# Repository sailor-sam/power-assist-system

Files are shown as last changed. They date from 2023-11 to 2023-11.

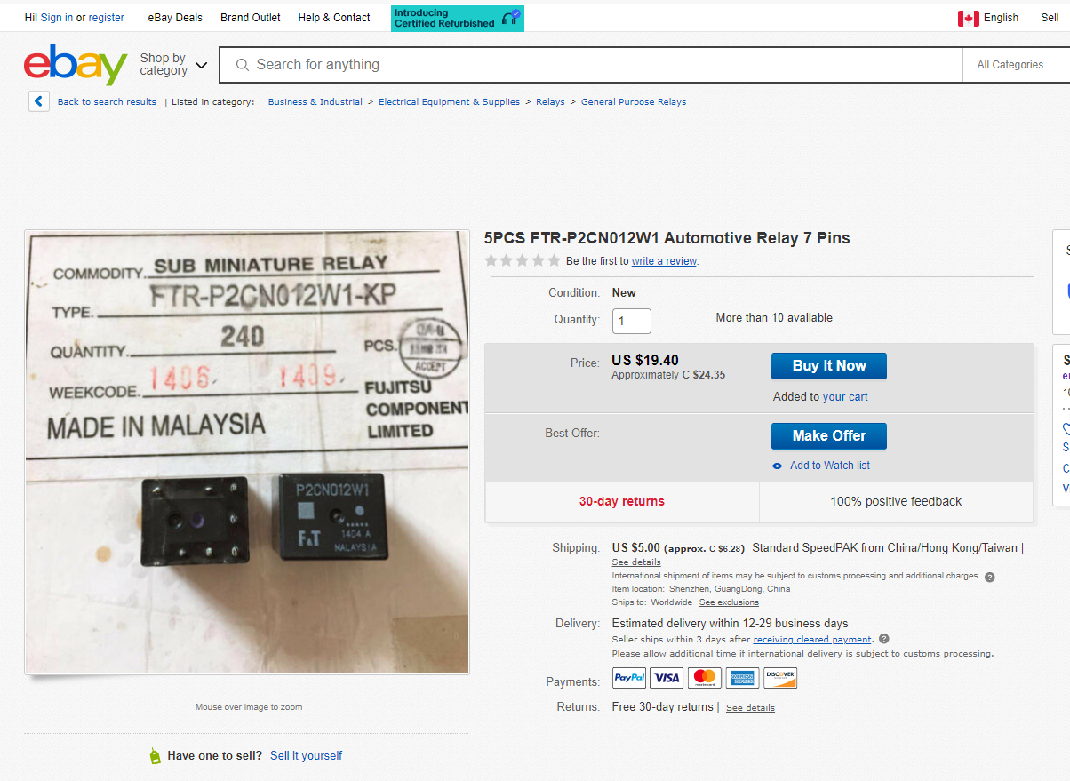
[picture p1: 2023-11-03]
module design files/joystick/Arduino_MKVI development/Fujitsu P2CN012W1 relay EBay.png

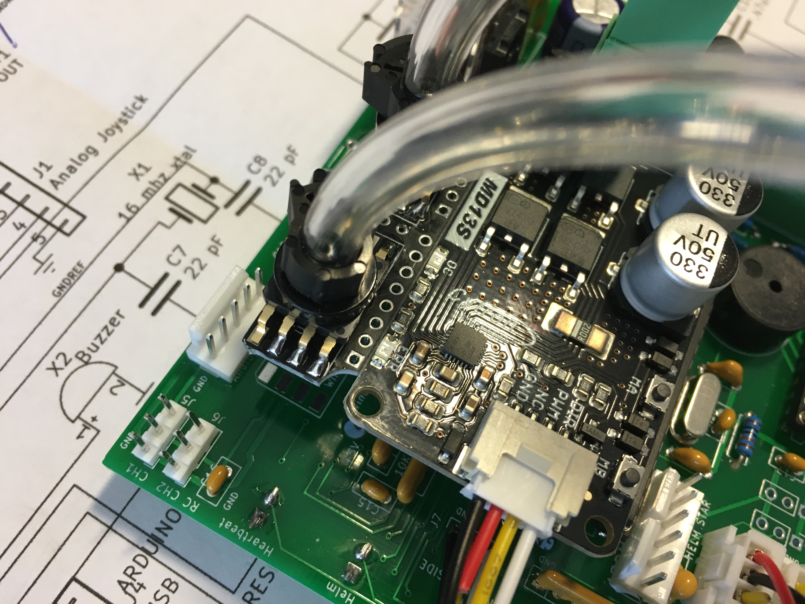
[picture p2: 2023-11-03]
module design files/joystick/Mk VI photos/MkVI SnP orientation 2.JPG

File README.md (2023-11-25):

# power-assist-system
Electronic servo motor system designed to assist people with severe  disabilities to control the helm and sail sheeting systems of a small  sailboat, via a sip&amp;puff or medical joystick interface.

Kevin and Rick Mercer

https://youtu.be/U6-sZrs9T38?si=PjePZXyoL59SkXcZ&t=115

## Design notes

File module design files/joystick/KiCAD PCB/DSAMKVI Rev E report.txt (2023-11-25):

Plot file "C:\Data files\Power Assist System\Product Design & Revision files\Mk VI Redesign 2023\DSAMKVIA KiCad\DSAMKVI REV B - E\DSAMKVIE-F_Cu.gbr" created.
Plot file "C:\Data files\Power Assist System\Product Design & Revision files\Mk VI Redesign 2023\DSAMKVIA KiCad\DSAMKVI REV B - E\DSAMKVIE-B_Cu.gbr" created.
Plot file "C:\Data files\Power Assist System\Product Design & Revision files\Mk VI Redesign 2023\DSAMKVIA KiCad\DSAMKVI REV B - E\DSAMKVIE-F_Paste.gbr" created.
Plot file "C:\Data files\Power Assist System\Product Design & Revision files\Mk VI Redesign 2023\DSAMKVIA KiCad\DSAMKVI REV B - E\DSAMKVIE-B_Paste.gbr" created.
Plot file "C:\Data files\Power Assist System\Product Design & Revision files\Mk VI Redesign 2023\DSAMKVIA KiCad\DSAMKVI REV B - E\DSAMKVIE-F_SilkS.gbr" created.
Plot file "C:\Data files\Power Assist System\Product Design & Revision files\Mk VI Redesign 2023\DSAMKVIA KiCad\DSAMKVI REV B - E\DSAMKVIE-F_Mask.gbr" created.
Plot file "C:\Data files\Power Assist System\Product Design & Revision files\Mk VI Redesign 2023\DSAMKVIA KiCad\DSAMKVI REV B - E\DSAMKVIE-B_Mask.gbr" created.
Plot file "C:\Data files\Power Assist System\Product Design & Revision files\Mk VI Redesign 2023\DSAMKVIA KiCad\DSAMKVI REV B - E\DSAMKVIE-Edge_Cuts.gbr" created.

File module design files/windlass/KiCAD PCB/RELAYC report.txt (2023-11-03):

Plot file "C:\Data files\Power Assist System\Product Design & Revision files\Mk VI design\RELAYB\RELAYC-F_Cu.gbr" created.
Plot file "C:\Data files\Power Assist System\Product Design & Revision files\Mk VI design\RELAYB\RELAYC-B_Cu.gbr" created.
Plot file "C:\Data files\Power Assist System\Product Design & Revision files\Mk VI design\RELAYB\RELAYC-F_Paste.gbr" created.
Plot file "C:\Data files\Power Assist System\Product Design & Revision files\Mk VI design\RELAYB\RELAYC-B_Paste.gbr" created.
Plot file "C:\Data files\Power Assist System\Product Design & Revision files\Mk VI design\RELAYB\RELAYC-F_SilkS.gbr" created.
Plot file "C:\Data files\Power Assist System\Product Design & Revision files\Mk VI design\RELAYB\RELAYC-F_Mask.gbr" created.
Plot file "C:\Data files\Power Assist System\Product Design & Revision files\Mk VI design\RELAYB\RELAYC-B_Mask.gbr" created.
Plot file "C:\Data files\Power Assist System\Product Design & Revision files\Mk VI design\RELAYB\RELAYC-Edge_Cuts.gbr" created.

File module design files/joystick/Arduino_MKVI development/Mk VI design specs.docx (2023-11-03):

3/31/21 pin 27 and 28 can be used for I2C in future

Pin | Description | 328Pin | UNO | Description | Function REVC
| +5V | 1 | RESET | PC6 | Reset
4 | USB TXD (or) Program Mode button | 2 | 0 | PD0 – IN | Digital Pin (RX)
5 | USB RXD | 3 | 1 | PD1 – OUT | Digital Pin (TX)
37 | RC1_input | 4 | 2 | PB0 – IN | Digital Pin
38 | RC2_input | 5 | 3 | PB1 – IN | Digital Pin (PWM)
23 | BUZZER | 6 | 4 | PD2 – OUT | Digital Pin
11 | VDD | 7 | | Vcc | Positive Voltage (Power)
12 | GND | 8 | | GND | Ground
13 | XTAL 1 | 9 | | XTAL 1 | Crystal Oscillator
14 | XTAL 2 | 10 | | XTAL 2 | Crystal Oscillator
21 | Windlass_LMP | 11 | 5 | PD5 – OUT | Digital Pin (PWM)
18 | Winch_OUT | 12 | 6 | PD6 – OUT | Digital Pin (PWM)
17 | Winch_IN | 13 | 7 | PD7 – OUT | Digital Pin
16 | PWM1_direction | 14 | 8 | PD3 – OUT | Digital Pin
15 | PWM1 helm | 15 | 9 | PD4 – OUT | Digital Pin (PWM)
22 | Bat_LOW_LED | 16 | 10 | PB2 – OUT | Digital Pin (PWM)
27 | Winch_LED | 17 | 11 | PB3 – OUT | Digital Pin (PWM)
28 | Helm_LED | 18 | 12 | PB4 – OUT | Digital Pin
29 | Heartbeat_LED | 19 | 13 | PB5 – OUT | Digital Pin
?? | AVCC | 20 | | AVCC | Positive voltage for ADC (power)
5 | Vref joystick | 21 | | AREF – IN | ADC Ref Voltage = Vcc
31 | GND | 22 | | GND | Ground
2 | Joystick helm | 23 | A0 | PC0 – IN | Analog Input
3 | Joystick wind | 24 | A1 | PC1 – IN | Analog Input
| S/P helm | 25 | A2 | PC2 – IN | Analog Input
| S/P wind | 26 | A3 | PC3 – IN | Analog Input
| Bat sensor | 27 | A4 | PC4 – IN | Analog Input SDA
4 | MODE | 28 | A5 | PC5 – IN | Analog Input SCL

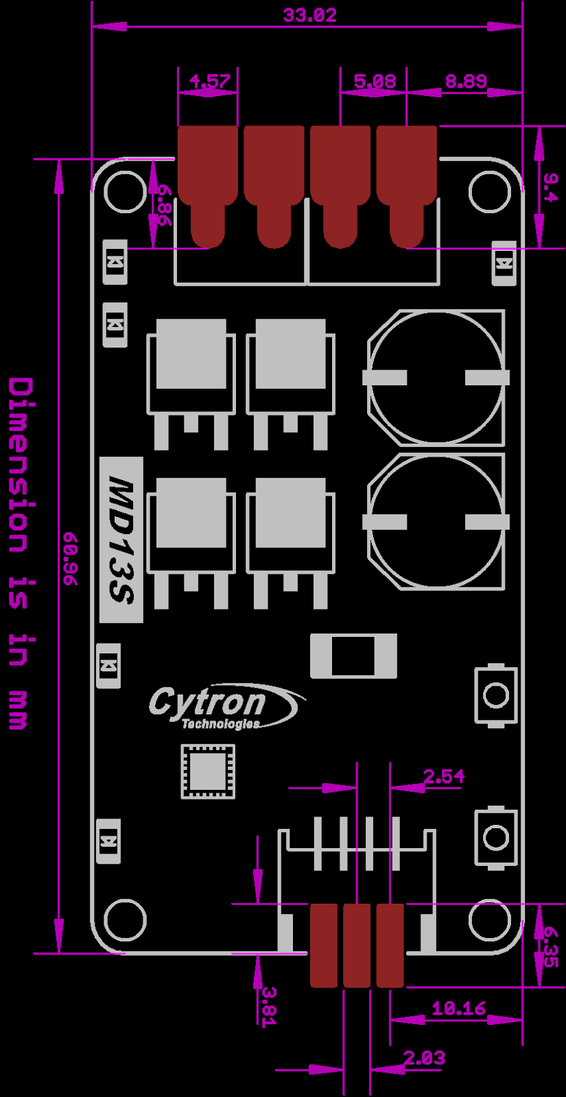
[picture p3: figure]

Remote RC: RadioLink T8S transmitter and R8EF Receiver

T8S transmitter must be configured via the RadioLink IPhone App.

Channels: For T8S, channels ONE (RC1 HELM) and THREE (RC2 WINCH) are connected to Mk VI PCB ports. Note that polarity of both T8S channels must be REVERSED.

RX Failsafe Mode: As long as it is powered by the mk VI, the R8EF cannot be configured to stop transmitting pulses to the Mk VI, whether or not a TX is present. Failsafe Mode (F/S) is set at 50% PWM. When TX is turned OFF (or out of range), PWM will be NEUTRAL and not interfere with joystick/sip and puff commands.

NOTE: while using RadioLink App, settings can only be changed when TX is disconnected (go figure!). 1) READ configuration from TX, 2) then DISCONNECT, 3) make changes, 4) then RECONNECT and WRITE changes to TX.

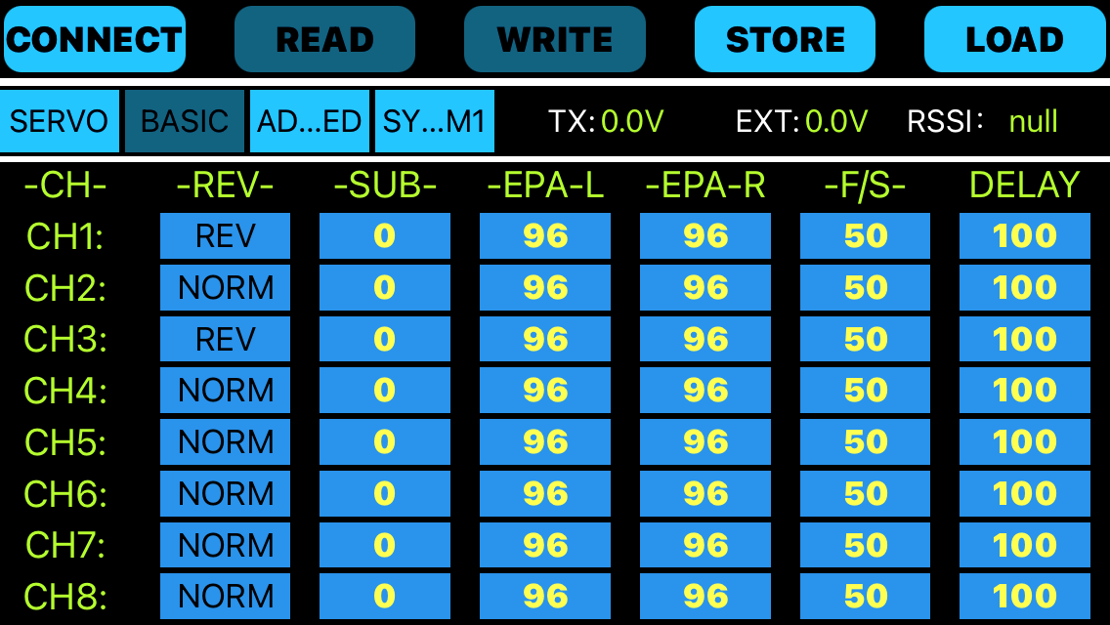
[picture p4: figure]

ATMega328 pinout

In this article, we will go over the pinout of the Atmega328 chip.

The Atmega328 is a very popular microcontroller chip produced by Atmel. It is an 8-bit microcontroller that has 32K of flash memory, 1K of EEPROM, and 2K of internal SRAM.

The Atmega328 is one of the microcontroller chips that are used with the popular Arduino Duemilanove boards. The Arduino Duemilanove board comes with either 1 of 2 microcontroller chips, the Atmega168 or the Atmega328. Of these 2, the Atmega328 is the upgraded, more advanced chip. Unlike the Atmega168 which has 16K of flash program memory and 512 bytes of internal SRAM, the Atmega328 has 32K of flash program memory and 2K of Internal SRAM.

The Atmega328 has 28 pins.

It has 14 digital I/O pins, of which 6 can be used as PWM outputs and 6 analog input pins. These I/O pins account for 20 of the pins.

The pinout for the Atmega328 is shown below.

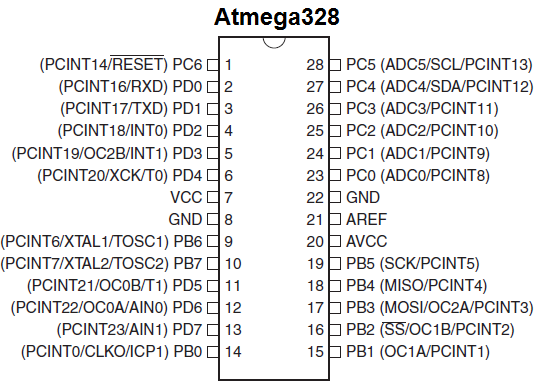
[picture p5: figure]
Atmega328 pinout

The table below gives a description for each of the pins, along with their function.

Pin Number | Description | Function
1 | PC6 | Reset
2 | PD0 | Digital Pin (RX)
3 | PD1 | Digital Pin (TX)
4 | PD2 | Digital Pin – EXT INT
5 | PD3 | Digital Pin (PWM) – EXT INT
6 | PD4 | Digital Pin
7 | Vcc | Positive Voltage (Power)
8 | GND | Ground
9 | XTAL 1 | Crystal Oscillator
10 | XTAL 2 | Crystal Oscillator
11 | PD5 | Digital Pin (PWM)
12 | PD6 | Digital Pin (PWM)
13 | PD7 | Digital Pin
14 | PB0 | Digital Pin
15 | PB1 | Digital Pin (PWM)
16 | PB2 | Digital Pin (PWM)
17 | PB3 | Digital Pin (PWM)
18 | PB4 | Digital Pin
19 | PB5 | Digital Pin
20 | AVCC | Positive voltage for ADC (power)
21 | AREF | Reference Voltage
22 | GND | Ground
23 | PC0 | Analog Input
24 | PC1 | Analog Input
25 | PC2 | Analog Input
26 | PC3 | Analog Input
27 | PC4 | Analog Input - I2C SDA
28 | PC5 | Analog Input – I2C SCL

As stated before, 20 of the pins function as I/O ports. This means they can function as an input to the circuit or as output. Whether they are input or output is set in the software. 14 of the pins are digital pins, of which 6 can function to give PWM output. 6 of the pins are for analog input/output.

2 of the pins are for the crystal oscillator. This is to provide a clock pulse for the Atmega chip. A clock pulse is needed for synchronization so that communication can occur in synchrony between the Atmega chip and a device that it is connected to.

The chip needs power so 2 of the pins, Vcc and GND, provide it power so that it can operate. The Atmega328 is a low-power chip, so it only needs between 1.8-5.5V of power to operate.

The Atmega328 chip has an analog-to-digital converter (ADC) inside of it. This must be or else the Atmega328 wouldn't be capable of interpreting analog signals. Because there is an ADC, the chip can interpret analog input, which is why the chip has 6 pins for analog input. The ADC has 3 pins set aside for it to function- AVCC, AREF, and GND. AVCC is the power supply, positive voltage, that for the ADC. The ADC needs its own power supply in order to work. GND is the power supply ground. AREF is the reference voltage that the ADC uses to convert an analog signal to its corresponding digital value. Analog voltages higher than the reference voltage will be assigned to a digital value of 1, while analog voltages below the reference voltage will be assigned the digital value of 0. Since the ADC for the Atmega328 is a 10-bit ADC, meaning it produces a 10-bit digital value, it converts an analog signal to its digital value, with the AREF value being a reference for which digital values are high or low. Thus, a portrait of an analog signal is shown by this digital value; thus, it is its digital correspondent value.

The last pin is the RESET pin. This allows a program to be rerun and start over.

And this sums up the pinout of an Atmega328 chip.

Related Resources

How to Use the LM741 Op Amp as a Comparator (http://www.learningaboutelectronics.com/Articles/LM741-op-amp-voltage-comparator.php)

How to Build an LM339 Quad Voltage Comparator Circuit (http://www.learningaboutelectronics.com/Articles/LM339-quad-voltage-comparator-circuit.php)

How to Build a Dark-activated Switch (http://www.learningaboutelectronics.com/Articles/Dark-activated-switch.php)

How to Build a Hall Effect Sensor Circuit (http://www.learningaboutelectronics.com/Articles/Hall-effect-sensor-circuit.php)

How to Build a Touch Sensor Circuit (http://www.learningaboutelectronics.com/Articles/How-to-build-a-touch-sensor-circuit)

How to Build an Accelerometer Circuit (http://www.learningaboutelectronics.com/Articles/Accelerometer-circuit.php)

How to Build a Motion Detector Circuit (http://www.learningaboutelectronics.com/Articles/Motion-detector-circuit.php)

How to Build a Motion Detector Alarm Circuit (http://www.learningaboutelectronics.com/Articles/Motion-detector-alarm-circuit.php)

23. Analog-to-Digital Converter

23.1 Features

● 10-bit resolution

● 0.5 LSB integral non-linearity

● ±2 LSB absolute accuracy

● 65 to 260µs conversion time

● Up to 15kSPS

● 6 multiplexed single ended input channels

● 2 additional multiplexed single ended input channels

● Temperature sensor input channel

● Optional left adjustment for ADC result readout

● 0 to VCC ADC input voltage range

● Selectable 1.1V ADC reference voltage

● Free running or single conversion mode

● Interrupt on ADC conversion complete

● Sleep mode noise canceler

23.2 Overview

The Atmel® ATmega328P features a 10-bit successive approximation ADC. The ADC is connected to an 8-channel analog multiplexer which allows eight single-ended voltage inputs constructed from the pins of Port A. The single-ended voltage inputs refer to 0V (GND).

The ADC contains a sample and hold circuit which ensures that the input voltage to the ADC is held at a constant level during conversion. A block diagram of the ADC is shown in Figure 23-1 on page 206.

The ADC has a separate analog supply voltage pin, AVCC. AVCC must not differ more than ±0.3V from VCC. See Section 23.6 “ADC Noise Canceler” on page 211 on how to connect this pin.

Internal reference voltages of nominally 1.1V or AVCC are provided on-chip. The voltage reference may be externally decoupled at the AREF pin by a capacitor for better noise performance.

The power reduction ADC bit, PRADC, in Section 9.10 “Minimizing Power Consumption” on page 36 must be disabled by writing a logical zero to enable the ADC.

The ADC converts an analog input voltage to a 10-bit digital value through successive approximation. The minimum value represents GND and the maximum value represents the voltage on the AREF pin minus 1 LSB.

Optionally, AVCC or an internal 1.1V reference voltage may be connected to the AREF pin by writing to the REFSn bits in the ADMUX register. The internal voltage reference may thus be decoupled by an external capacitor at the AREF pin to improve noise immunity.

# Digital Pins

The pins on the Arduino can be configured as either inputs or outputs. This document explains the functioning of the pins in those modes. While the title of this document refers to digital pins, it is important to note that vast majority of Arduino (Atmega) analog pins, may be configured, and used, in exactly the same manner as digital pins.

### Properties of Pins Configured as INPUT

Arduino (Atmega) pins default to inputs, so they don't need to be explicitly declared as inputs with pinMode() when you're using them as inputs. Pins configured this way are said to be in a high-impedance state. Input pins make extremely small demands on the circuit that they are sampling, equivalent to a series resistor of 100 megohm in front of the pin. This means that it takes very little current to move the input pin from one state to another, and can make the pins useful for such tasks as implementing a capacitive touch sensor (https://www.arduino.cc/playground/Code/CapacitiveSensor), reading an LED as a photodiode (https://www.arduino.cc/playground/Learning/LEDSensor), or reading an analog sensor with a scheme such as RCTime. (https://www.arduino.cc/en/Tutorial/RCtime)

This also means however, that pins configured as pinMode(pin, INPUT) with nothing connected to them, or with wires connected to them that are not connected to other circuits, will report seemingly random changes in pin state, picking up electrical noise from the environment, or capacitively coupling the state of a nearby pin.

### Pullup Resistors with pins configured as INPUT

Often it is useful to steer an input pin to a known state if no input is present. This can be done by adding a pullup resistor (to +5V), or a pulldown resistor (resistor to ground) on the input. A 10K resistor is a good value for a pullup or pulldown resistor.

### Properties of Pins Configured as INPUT_PULLUP

There are 20K pullup resistors built into the Atmega chip that can be accessed from software. These built-in pullup resistors are accessed by setting the pinMode() as INPUT_PULLUP. This effectively inverts the behavior of the INPUT mode, where HIGH means the sensor is off, and LOW means the sensor is on.

The value of this pullup depends on the microcontroller used. On most AVR-based boards, the value is guaranteed to be between 20kΩ and 50kΩ. On the Arduino Due, it is between 50kΩ and 150kΩ. For the exact value, consult the datasheet of the microcontroller on your board.

When connecting a sensor to a pin configured with INPUT_PULLUP, the other end should be connected to ground. In the case of a simple switch, this causes the pin to read HIGH when the switch is open, and LOW when the switch is pressed.

The pullup resistors provide enough current to dimly light an LED connected to a pin that has been configured as an input. If LEDs in a project seem to be working, but very dimly, this is likely what is going on.

The pullup resistors are controlled by the same registers (internal chip memory locations) that control whether a pin is HIGH or LOW. Consequently, a pin that is configured to have pullup resistors turned on when the pin is an INPUT, will have the pin configured as HIGH if the pin is then switched to an OUTPUT with pinMode(). This works in the other direction as well, and an output pin that is left in a HIGH state will have the pullup resistors set if switched to an input with pinMode().

Prior to Arduino 1.0.1, it was possible to configure the internal pull-ups in the following manner:

pinMode(pin, INPUT); // set pin to input

digitalWrite(pin, HIGH); // turn on pullup resistors

NOTE: Digital pin 13 is harder to use as a digital input than the other digital pins because it has an LED and resistor attached to it that's soldered to the board on most boards. If you enable its internal 20k pull-up resistor, it will hang at around 1.7V instead of the expected 5V because the onboard LED and series resistor pull the voltage level down, meaning it always returns LOW. If you must use pin 13 as a digital input, set its pinMode() to INPUT and use an external pull down resistor.

### Properties of Pins Configured as OUTPUT

Pins configured as OUTPUT with pinMode() are said to be in a low-impedance state. This means that they can provide a substantial amount of current to other circuits. Atmega pins can source (provide positive current) or sink (provide negative current) up to 40 mA (milliamps) of current to other devices/circuits. This is enough current to brightly light up an LED (don't forget the series resistor), or run many sensors, for example, but not enough current to run most relays, solenoids, or motors.

Short circuits on Arduino pins, or attempting to run high current devices from them, can damage or destroy the output transistors in the pin, or damage the entire Atmega chip. Often this will result in a "dead" pin in the microcontroller but the remaining chip will still function adequately. For this reason it is a good idea to connect OUTPUT pins to other devices with 470Ω or 1k resistors, unless maximum current draw from the pins is required for a particular application.

# analogRead()

[Analog I/O]

### Description

Reads the value from the specified analog pin. Arduino boards contain a multichannel, 10-bit analog to digital converter. This means that it will map input voltages between 0 and the operating voltage(5V or 3.3V) into integer values between 0 and 1023. On an Arduino UNO, for example, this yields a resolution between readings of: 5 volts / 1024 units or, 0.0049 volts (4.9 mV) per unit. See the table below for the usable pins, operating voltage and maximum resolution for some Arduino boards.

The input range can be changed using analogReference() (https://www.arduino.cc/reference/en/language/functions/analog-io/analogreference), while the resolution can be changed (only for Zero, Due and MKR boards) using analogReadResolution().

On ATmega based boards (UNO, Nano, Mini, Mega), it takes about 100 microseconds (0.0001 s) to read an analog input, so the maximum reading rate is about 10,000 times a second.

BOARD | OPERATING VOLTAGE | USABLE PINS | MAX RESOLUTION
Uno | 5 Volts | A0 to A5 | 10 bits
Mini, Nano | 5 Volts | A0 to A7 | 10 bits
Mega, Mega2560, MegaADK | 5 Volts | A0 to A14 | 10 bits
Micro | 5 Volts | A0 to A11* | 10 bits
Leonardo | 5 Volts | A0 to A11* | 10 bits
Zero | 3.3 Volts | A0 to A5 | 12 bits**
Due | 3.3 Volts | A0 to A11 | 12 bits**
MKR Family boards | 3.3 Volts | A0 to A6 | 12 bits**

*A0 through A5 are labelled on the board, A6 through A11 are respectively available on pins 4, 6, 8, 9, 10, and 12
**The default analogRead() resolution for these boards is 10 bits, for compatibility. You need to use analogReadResolution() (https://www.arduino.cc/reference/en/language/functions/zero-due-mkr-family/analogreadresolution) to change it to 12 bits.

### Syntax

analogRead(pin)

### Parameters

pin: the name of the analog input pin to read from (A0 to A5 on most boards, A0 to A6 on MKR boards, A0 to A7 on the Mini and Nano, A0 to A15 on the Mega).

### Returns

The analog reading on the pin. Although it is limited to the resolution of the analog to digital converter (0-1023 for 10 bits or 0-4095 for 12 bits). Data type: int.

### Example Code

The code reads the voltage on analogPin and displays it.

int analogPin = A3; // potentiometer wiper (middle terminal) connected to analog pin 3

// outside leads to ground and +5V

int val = 0; // variable to store the value read

void setup() {

Serial.begin(9600); // setup serial

}

void loop() {

val = analogRead(analogPin); // read the input pin

Serial.println(val); // debug value

}

### Notes and Warnings

If the analog input pin is not connected to anything, the value returned by analogRead() will fluctuate based on a number of factors (e.g. the values of the other analog inputs, how close your hand is to the board, etc.).

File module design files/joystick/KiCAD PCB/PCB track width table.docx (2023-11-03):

PCB track width table

I got this off a ruler that Digikey sent out. The ruler is full of stuff pertaining to pcb layout.

0.5 oz copper

Mil vs degrees centigrade rise of conductor

Mil 1 5 10 20

6 0.13 0.27 0.37 0.50

10 0.19 0.39 0.53 0.72

15 0.26 0.53 0.72 0.97

20 0.32 0.65 0.88 1.20

30 0.43 0.87 1.18 1.61

40 0.53 1.07 1.46 1.98

50 0.62 1.26 1.71 2.32

75 0.83 1.69 2.30 3.12

100 1.03 2.09 2.83 3.84

150 1.38 2.80 3.80 5.16

200 1.70 3.45 4.68 6.35

At least some idea

cheers, Mark

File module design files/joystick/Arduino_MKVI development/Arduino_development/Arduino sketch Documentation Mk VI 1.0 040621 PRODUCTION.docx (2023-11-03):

/* POWER-ASSIST SYSTEM - MK VI SOFTWARE ************** ARDUINO UNO (ATMEGA328) APRIL 2021 ***************************************************

*

* BY: Project Manager: Steve Alvey 403-870-7210

* SW developer: Steve Alvey 403-870-7210

*

* VERSION: 1.0RC POWER-ASSIST MK VI

* Compatible with Mk VI REVC PCB (2021)

*

* PURPOSE: The POWER-ASSIST System provides control of HELM and WINCH 12V DC servo motors, to

* control sails and steering system of small sailboats. Sailors with limited

* hand function may control the Autohelm System via a wheelchair style joystick or Sip & Puff interface.

* For safety, an (optional) RC Remote joystick is supported. When in use, commands received from the RC Remote Control

* are given priority over operator joysitck or sip and puff commands. Once ANY RC input command is received,

* Joystick and sip and puff commands are ignored for ONE SECOND. After ONE SECOND, joystick and sip and puff commands

* will be handled.

* See www.accessiblesailingtechnology.com for pictures and Power Assist System Operator Manual.

*

* LAST CHANGED: 4/06/21 S ALVEY - initial PRODUCTION BUILD tested and certified

* Outstanding issues: NONE

*

* NOTES:

* 1. N.O. pushbutton is connected to pin 1, to be used for future programming of MODES (programming LED present)

* 2. pin 28 has tri-state input jumper, for use as hardware MODE input

* 3. I2C interface may be added to pins A4 and A5 in future

*

*

* GENERAL DESCRIPTION OF S/W:

*

* This software performs five functions continuously, four in the MAIN loop and the RC inputs via Interupt Service Routines (ISR):

*

* readbattery(); Battery voltage is polled continuously. When less than 12.V, Battery Low LED is flashed.

* When less than 11.5V, Battery Low LED is ON and buzzer is ON as a warning to the Operator.

* If battery voltage remains below 11.5V for more than ONE MINUTE, Helm and Winch outputs are disabled. Battery Low LED and buzzer remain ON.

*

* checkInputs(); The Arduino receives inputs from one of THREE SOURCES: A joystick on the Module; Sip & Puff sensors; or a remote control RC Joystick

* Input commands are polled continuously and executed (one at a time), in priority: RC joystick commands are PRIORITY ONE and

* will override conflicting joystick or sipp & puff commands received within ONE SECOND.

* When a valid input command is received, that command must be released before any NEW command will be accepted.

* Although the sip&puff and RC joystick inputs are analog (proportional), all inputs are sensed and decoded as BINARY,

* once they exceed a "deadband" threshold. The deadband varies for each INPUT to establish an ergonomic sensitivity for that input device.

* (i.e. joystick sensitivity is NOMINAL; sip & puff sensitivity is INCREASED; RC joystick sensitivity is DECREASED).

*

* handleInputCommand(); When an input command is received, it is decoded (joystick position) and then passed to be handled by handleInputCommand routine.

* The HELM or WINCH actuator is activated in the appropriate direction for the period the INPUT is present. Only ONE INPUT will be handled at a time.

* The HELM output is a proportional PWM drive for brushed DC motor, generating PWM (ANALOG) and PWM DIRECTION (DIGITAL) outputs.

* Since all inputs are decoded as BINARY, the use of PWM proportional output is limited to the implementation of a "soft start" for the DC motor (PWM 'ramp').

* The WINCH output actuates a DC Relay, located remotely. Two active HIGH signals: WINCHIN and WINCHOUT are generated on DIGITAL outputs, and

* then inverted by a ULN2003 driver to actuate the DC Relay.

*

* heartbeat_LED(); The heartbear LED 'blinks' at 1 Hz, indicating the Arduino is running. When an INPUT is present, the buzzer is activated at a 1 Hz rate,

* providing audio feedback to the Operator. The buzzer is also used to warn the Operator that the battery is LOW.

*

* RC1/2_Input; A remote control RC Joystick is an (optional) 'plug-n-play' device. When installed on the Mk VI PCB, the RC Receiver will generate two independent RC channels

* (HELM = RC Receiver CH1, WINCH = RC Receiver CH3), each channel producing an PWM signal (RC standard: 1 - 2ms pulse at 50 Hz rate; 1.5ms nominal).

* Interupt Service Routines timeRC1Pulse and timeRC2Pulse provide critical timing of the PWM pulse duration by synchronizing

* with the rising and falling edges of each PWM pulse. These values are passed to the checkInputs routine for decoding.

**************************************************************************************************************************************************/

/***********************************************

/ define ATMega328 pins

/**********************************************/

#define interrupts()

#define USB_TXD 0 // O PD0

#define PROGRAM 0 // O PD0

#define USB_RXD 1 // I PD1

#define RC1_INPUT 2 // I PB0

#define RC2_INPUT 3 // I PB1

#define BUZZER 4 // O PD4

#define WINDLASS_LMP 5 // O PD5

#define WINCH_OUT 6 // O PD6

#define WINCH_IN 7 // O PD7

#define PWM1_DIRECTION 8 // O PD4

#define PWM1 9 // O PD3

#define BAT_LOW_LED 10 // O PB2

#define WINCH_LED 11 // O PB3

#define HELM_LED 12 // O PB4

#define HEARTBEAT_LED 13 // O PB5

#define JOYSTICK_HELM A0 // I PC0

#define JOYSTICK_WIND A1 // I PC1

#define SIPPUFF_HELM A2 // I PC2

#define SIPPUFF_WIND A3 // I PC3

#define BATTERY A4 // I PC4

#define MODE A5 // I PC4

/***********************************************

/ C++ function declarations

/**********************************************/

void readbattery(void);

void allOff(void);

byte checkInputs(void);

void handleInputCommand(void);

void heartbeat_LED(void);

/***********************************************

/ constants/variables for heartbeat timer routine

/**********************************************/

int ledState = LOW; // 'state' variable used to set the LED

bool beep = false; // boolean 'state' variable to activate BUZZER

unsigned long currentMicros = 0; // read the current time...

unsigned long previousMillis = 0; // store last time LED 'state' was changed

const long blink_interval = 500; // set LED 'blink' interval (milliseconds)

/***********************************************

/ constants/variables for joystick routine

/**********************************************/

byte JOY_POS = 5; // joystick position: joy CENTER (no input) = 5; joy RIGHT = 4; joy LEFT = 3; joy UP = 2; joy DOWN = 1

int joy_LR = 0; // variable for joystick helm value

int snp_LR = 0; // variable for sip and puff helm value

int joy_UD = 0; // variable for joystick winch value

int snp_UD = 0; // variable for sip and puff winch value

const int J_REF = 512; // set the centerpoint of joystick ADC

const int deadband = 100; // set joystick ADC deadband (512 +/- 100)

/**********************************************************************

/ constants/variables for battery meter routine

/*********************************************************************/

int battery_V = 0; // variable for battery voltage

byte beepState = LOW; // 'state' variable used to set the BUZZER

byte deadBatteryState = LOW; // 'state' variable used for dead battery voltage (less than 11.5V)

const int batterylow = 770; // set battery low constant @ 12.2V

const int batterydead = 725; // set battery dead constant @ 11.5V

unsigned long Battery_State_timer = 0; // timer used to measure duration of "dead battery" state

unsigned long Dead_Battery_detected = 0;// record the time when "dead battery" state (< 11.5V) is first detected; RESET this time whenever battery voltage recovers to ABOVE "dead battery" state (< 11.5V)

/***********************************************

/ constants/variables for RC input routine

/**********************************************/

int RC1_Pin = 0; // variable for reading RC1 pin

int RC2_Pin = 0; // variable for reading RC2 pin

int RC1_Value = 512; // variable for RC joystick winch value (512 = neutral)

int RC2_Value = 512; // variable for RC sip and puff winch value (512 = neutral)

unsigned long RC_NEUTRAL = 1500; // RC reference value, equivalent to 1.5msec pulsewidth

const long max_pulse_length = 2000; // longest valid pulse length is 2.0 msec

const long min_pulse_length = 500; // shortest valid pulse length is 500 millisec

bool startflag_RC1_Pulse = true;

bool startflag_RC2_Pulse = true;

byte bad_RC1_pulse = 0; // declared, but not used 040321

byte bad_RC2_pulse = 0; // declared, but not used 040321

unsigned long startofPulse = 0; // record the time of the 'start' of an RC pulse

unsigned long RC_priority_interval = 1000; // RC Commands are given PRIORITY. Once a command is received, joystick and s&p commands are

disabled for RC_priority_interval (ONE second = 1,000 milliseconds)

unsigned long RC_Command_received = 0; // initialized (0) each time RC command is received

/******************************************************

/ constants/variables for PWM output generation

/******************************************************/

byte pwm_value = 0; // value from 0 - 255 for PWM speed

byte pwm_dir = 0; // value 1 or 0 for direction

const byte ramp_inc = 2; // set joystick pwm ramp increment to implement 'soft start' of HELM actuator

/******************************************************************************************************************************/

void setup() //execute setup ONCE at start up, to initialize system states

{

pinMode(PROGRAM, INPUT); // button switch for programming/debugging

pinMode(JOYSTICK_HELM, INPUT); // joystick helm

pinMode(JOYSTICK_WIND, INPUT); // joystick windlass

pinMode(RC1_INPUT, INPUT); // joystick helm

pinMode(RC2_INPUT, INPUT); // joystick windlass

pinMode(SIPPUFF_HELM, INPUT); // joystick helm

pinMode(SIPPUFF_WIND, INPUT); // joystick windlass

pinMode(BATTERY, INPUT); // Battery voltage sense

pinMode(MODE, INPUT); // mode sense (tri-state)

pinMode(HEARTBEAT_LED, OUTPUT); // Heartbeat LED

pinMode(BAT_LOW_LED, OUTPUT); // Bat Low LED

pinMode(WINCH_LED, OUTPUT); // Winch LED

pinMode(HELM_LED, OUTPUT); // Helm LED

pinMode(WINDLASS_LMP, OUTPUT); // Remote LED on Windlass

pinMode(BUZZER, OUTPUT); // Piezo Buzzer

pinMode(PWM1, OUTPUT); // PWM1 helm

pinMode(PWM1_DIRECTION, OUTPUT); // PWM1_direction helm

Serial.begin(115200);

while(!Serial); // wait until SERIAL link is established....

setPwmFrequency(PWM1, 8); // increase Arduino PWM frequency to 3.9 KHz

attachInterrupt(digitalPinToInterrupt(RC1_INPUT),timeRC1pulse,CHANGE); // attach interrupt handler for RC1_INPUT. ISR called on both RISING and FALLING edge of PWM pulse

attachInterrupt(digitalPinToInterrupt(RC2_INPUT),timeRC2pulse,CHANGE); // attach interrupt handler for RC2_INPUT. ISR called on both RISING and FALLING edge of PWM pulse

allOff(); // initialize all outputs to OFF

} // END of setup()

/*************************************************************************************************************************/

/********************************************

* CHANGE ARDUINO PWM FREQUENCY * Allows Arduino PWM frequency to be raised from 488 Hz to 3.9 KHz for higher motor efficiency

********************************************/

void setPwmFrequency(int pin, int divisor)

{

byte mode;

if(pin == 5 || pin == 6 || pin == 9 || pin == 10) {

switch(divisor) {

case 1: mode = 0x01; break;

case 8: mode = 0x02; break;

case 64: mode = 0x03; break;

case 256: mode = 0x04; break;

case 1024: mode = 0x05; break;

default: return;

}

if(pin == 5 || pin == 6) {

TCCR0B = TCCR0B & 0b11111000 | mode;

} else {

TCCR1B = TCCR1B & 0b11111000 | mode;

}

} else if(pin == 3 || pin == 11) {

switch(divisor) {

case 1: mode = 0x01; break;

case 8: mode = 0x02; break;

case 32: mode = 0x03; break;

case 64: mode = 0x04; break;

case 128: mode = 0x05; break;

case 256: mode = 0x06; break;

case 1024: mode = 0x07; break;

default: return;

}

TCCR2B = TCCR2B & 0b11111000 | mode;

}

}

/*****************************************

* turn ALL off (MULTIPLE CALLS) *

*****************************************/

void allOff()

{

JOY_POS = 5; // turn helm drive OFF

pwm_value = 0; // turn helm drive OFF

RC1_Value = J_REF;

RC2_Value = J_REF;

digitalWrite(PWM1_DIRECTION, pwm_dir);

analogWrite(PWM1, pwm_value);

digitalWrite(HELM_LED, LOW);

digitalWrite(WINCH_OUT, LOW); // TURN OFF WINCH AND WINCH LED

digitalWrite(WINCH_IN, LOW);

digitalWrite(WINCH_LED, LOW);

beep = false;

}

/******************************************** check battery voltage continuously

* BATTERY METER ROUTINE * when battery voltage drops below 12.2V, indicate with Battery Low LED flashing

******************************************** when battery volatge drops below 11.5V, indicate with Battery Low LED ON, and buzzer ON

If battery voltage remians below 11.5V for more than ONE MINUTE, all outputs will be turned OFF to protect battery */

void readbattery()

{

unsigned long Battery_State_timer = millis(); // update Battery_State_timer

battery_V = analogRead(BATTERY);

if (battery_V < batterylow && battery_V > batterydead) // if battery V greater than 11.5V but less than 12.2V: Battery Low LED flashing as "low battery" warning

{

digitalWrite(BAT_LOW_LED, ledState);

Dead_Battery_detected = millis(); //reset Dead_Battery_detected timer

}

else if (battery_V < batterydead) // if battery V less than 11.5V (dead): Battery Low LED on full, BUZZER on as "dead battery" warning.

Then, if 'dead' voltage condition (< 11.5V) remains for ONE MINUTE, turn all outputs OFF (allOFF).

{

digitalWrite(BAT_LOW_LED, HIGH);

digitalWrite(BUZZER, HIGH);

if ((Battery_State_timer - Dead_Battery_detected) >= 60000) // if 'dead' voltage condition (< 11.5V) remains for ONE MINUTE (60,000 milliseconds), turn all outputs OFF (allOFF).

{

allOff();

}

}

else

{

digitalWrite(BAT_LOW_LED, LOW); // if battery V more than 12.2V: Battery OK

Dead_Battery_detected = millis(); //reset Dead_Battery_detected timer

}

}

/******************************************** check for joystick, RC, Sip & Puff input command

* CHECK INPUT COMMANDS * RC Joystick is offered as an optional SAFETY device, for Disabled Sailing Program Operator.

******************************************** if RC Joystick (option) is present and turned ON, these commands will be given PRIORITY over a sailor's joystick or sip & puff commands */

byte checkInputs()

{

unsigned long RC_Priority_timer = millis(); // RC Commands are given PRIORITY ONE. Once an RC command is received, joystick and s&p commands are disabled for ONE second

joy_LR = analogRead(JOYSTICK_HELM);

snp_LR = analogRead(SIPPUFF_HELM);

joy_UD = (1024 - analogRead(JOYSTICK_WIND)); // NOTE: reverse polarity of joystick up/down

snp_UD = (analogRead(SIPPUFF_WIND));

if (RC1_Value > (J_REF + (deadband*2))) // RC joystick deflection (PRIOIRTY ONE) greater than deadband = HELM PORT COMMAND

{

JOY_POS = 3;

RC_Command_received = millis();

return;

}

else if (RC1_Value < (J_REF - (deadband*2))) // RC joystick deflection (PRIOIRTY ONE) less than deadband = HELM STARBOARD COMMAND

{

JOY_POS = 4;

RC_Command_received = millis();

return;

}

else if (RC2_Value > (J_REF + (deadband*3))) // RC joystick deflection (PRIOIRTY ONE) greater than deadband = WINCH OUT COMMAND

{

JOY_POS = 1;

RC_Command_received = millis();

return;

}

else if (RC2_Value < (J_REF - (deadband*3))) // RC joystick deflection (PRIOIRTY ONE) less than (neg) deadband = WINCH IN COMMAND

{

JOY_POS = 2;

RC_Command_received = millis();

return;

}

if ((RC_Priority_timer - RC_Command_received) >= RC_priority_interval) // RC Commands are given PRIORITY ONE. Once an RC command is received,

joystick and s&p commnads are disabled for RC_priority_interval (ONE second)

{

if ((joy_LR > (J_REF + deadband)) || (snp_LR > (J_REF + (deadband/2)))) // joystick deflection (or sip/puff) (PRIORITY TWO) greater than deadband = HELM PORT COMMAND

{

JOY_POS = 3;

return;

}

else if ((joy_LR < (J_REF - deadband)) || (snp_LR < (J_REF - (deadband/2)))) // joystick deflection (or sip/puff) (PRIORITY TWO) less than deadband = HELM STARBOARD COMMAND

{

JOY_POS = 4;

return;

}

else if ((joy_UD > (J_REF + deadband)) || (snp_UD > (J_REF + (deadband/2)))) // joystick deflection (or sip/puff) (PRIORITY TWO) greater than deadband = WINCH OUT COMMAND

{

JOY_POS = 1;

return;

}

else if ((joy_UD < (J_REF - deadband)) || (snp_UD < (J_REF - (deadband/2)))) // joystick deflection (or sip/puff) (PRIORITY TWO) less than (neg) deadband = WINCH IN COMMAND

{

JOY_POS = 2;

return;

}

}

}

/******************************************** when input command received, execute requested OUTPUT

* HANDLE INPUT COMMANDS * for safety, only one OUTPUT command can be executed at one time

*******************************************/

void handleInputCommand()

{

//Serial.println(JOY_POS);

switch(JOY_POS)

{

case 1:

{

digitalWrite(WINCH_OUT, HIGH); // if Joystick position = 1, actuate WINCH OUT

digitalWrite(WINCH_LED, HIGH);

beep = true;

JOY_POS = 5; // command complete; RESET joystick position flag

break;

}

case 2:

{

digitalWrite(WINCH_IN, HIGH); // if Joystick position = 2, actuate WINCH IN

digitalWrite(WINCH_LED, HIGH);

beep = true;

JOY_POS = 5; // command complete; RESET joystick position flag

break;

}

case 3:

{

pwm_dir = 1; // if Joystick position = 3, actuate HELM to port

if (pwm_value < 250) // pwm output value is 'ramped' from 0 - 255 to implement 'soft start' for HELM output

{

pwm_value = (pwm_value + ramp_inc); // increment 'pwm ramp' value

beep = true;

delay(1);

}

else

{

pwm_value = 255; // go FULL SPEED

beep = true;

}

digitalWrite(PWM1_DIRECTION, pwm_dir);

analogWrite(PWM1, pwm_value);

digitalWrite(HELM_LED, HIGH);

JOY_POS = 5; // command complete; RESET joystick position flag

break;

}

case 4:

{

pwm_dir = 0; // if Joystick position = 4, actuate HELM to starboard

if (pwm_value < 250) // pwm output value is 'ramped' from 0 - 255 to implement 'soft start' for HELM output

{

pwm_value = (pwm_value + ramp_inc); // increment 'pwm ramp' value

beep = true;

delay(1);

}

else

{

pwm_value = 255; // go FULL SPEED

beep = true;

}

digitalWrite(PWM1_DIRECTION, pwm_dir);

analogWrite(PWM1, pwm_value);

digitalWrite(HELM_LED, HIGH);

JOY_POS = 5; // command complete; RESET joystick position flag

break;

}

case 5: // if Joystick position = 5; no INPUT is present

{

allOff(); // turn all outputs OFF

break;

}

}

}

/******************************************** check to see if it's time to blink the LED: that is, if the difference

* HEARTBEAT LED ROUTINE * between the current time and last time you blinked the LED is greater than

******************************************** the 'blink' period (blink_interval) */

void heartbeat_LED()

{

unsigned long currentMillis = millis(); // read the current time...

if (currentMillis - previousMillis >= blink_interval) // once 'blink_interval' time reached....

{

previousMillis = currentMillis; // ....save the last time you blinked the LED and then....

if (ledState == LOW)

{

ledState = HIGH; // ....toggle state

if (beep == true) beepState = true;

else beepState = false;

}

else

{

ledState = LOW;

beepState = false;

}

digitalWrite(HEARTBEAT_LED, ledState); // write the HEARTBEAT LED with 'ledState'

digitalWrite(WINDLASS_LMP, ledState);

digitalWrite(BUZZER, beepState); // write the BUZZER with 'beepState'

}

}

/******************************************** // synchronize with the rising edge of RC1 pulse, then measure pulse width

* RC1 INPUT INTERUPT SERVICE ROUTINE *

*******************************************/

void timeRC1pulse()

{

noInterrupts();

if ((digitalRead (RC1_INPUT) == HIGH) && (startflag_RC1_Pulse == true)) // if interupt is RISING edge of new PWM pulse, record time of start of PWM pulse

{

startofPulse = micros();

startflag_RC1_Pulse = false;

interrupts();

return;

}

else // if interupt is FALLING edge of PWM pulse, validate and then measure width of PWM pulse

{

currentMicros = micros();

RC1_Value = (currentMicros - startofPulse);

if ((RC1_Value > max_pulse_length)||(RC1_Value < min_pulse_length))

{

bad_RC1_pulse = 1; // validate pulse width > min_pulse_length

RC1_Value = 512;

}

else

{

RC1_Value = constrain(RC1_Value, 1000, 2000); // CONSTRAIN pulse width to VALID range (1000 - 2000 microsec)

RC1_Value = map(RC1_Value, 1000, 2000, 0, 1024); // finally, SHIFT final RC value to VALID input range (comparable to joystick and sip and puff input range of 0 - 1024)

}

startflag_RC1_Pulse = true; // prepare to receive next PWM pulse

interrupts();

}

}

/******************************************** // synchronize with the rising edge of RC2 pulse, then measure pulse width

* RC2 INPUT INTERUPT SERVICE ROUTINE *

*******************************************/

void timeRC2pulse()

{

noInterrupts();

if ((digitalRead (RC2_INPUT) == HIGH) && (startflag_RC2_Pulse == true)) // if interupt is RISING edge of new PWM pulse, recond time of start of PWM pulse

{

startofPulse = micros();

startflag_RC2_Pulse = false;

interrupts();

return;

}

else // if interupt is FALLING edge of PWM pulse, validate and then measure width of PWM pulse

{

currentMicros = micros();

RC2_Value = (currentMicros - startofPulse);

if ((RC2_Value > max_pulse_length)||(RC2_Value < min_pulse_length))

{

bad_RC2_pulse = 1; // validate pulse width > min_pulse_length

RC2_Value = 512;

}

else

{

RC2_Value = constrain(RC2_Value, 1000, 2000); // CONSTRAIN pulse width to VALID range (1000 - 2000 microsec)

RC2_Value = map(RC2_Value, 1000, 2000, 0, 1024); // finally, SHIFT final RC value to VALID input range (comparable to joystick and sip and puff input range of 0 - 1024)

}

startflag_RC2_Pulse = true; // prepare to receive next PWM pulse

interrupts();

}

}

/********************************************

*

* MAIN PROGRAM LOOP * MAIN program loop; executes continuously

*

******************************************/

void loop()

{

readbattery(); // battery voltage is polled continuously. When less than 12.2V, Battery Low LED is flashed. When less than 11.5V, Battery Low LED is ON and buzzer is ON; HELM and WINCH are disabled.

checkInputs(); // Input commands are polled continuously; for safety, RC commands are PRIORITY ONE and override conflicting joystick and sipp & puff commands for ONE second

handleInputCommand(); // when present, input commands are handled by actuating HELM or WINCH as required

heartbeat_LED(); // heartbeat LED is blinked at 1 Hz; buzzer is activated when input command is present

}

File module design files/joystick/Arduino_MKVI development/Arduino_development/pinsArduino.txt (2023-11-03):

#define 	RESET	  	1	// I  PC6
#define 	USB TXD		2	// O  PD0
#define 	USB RXD   	3	// I  PD1
#define 	BUZZER    	4	// O  PD4
#define 	PWM1     	5	// O  PD3
#define 	PWM1_DIRECTION 	6	// O  PD4
#define 	WINDLASS_LMP 	11	// O  PD5
#define 	WINCH_OUT 	12	// O  PD6
#define 	WINCH_IN  	13	// O  PD7
#define 	RC1_INPUT	14	// I  PB0
#define 	RC2_INPUT	15	// I  PB1
#define 	BAT_LOW_LED  	16	// O  PB2
#define		WINCH_LED	17	// O  PB3
#define		HELM_LED  	18	// O  PB4
#define		HEARTBEAT_LED 	19	// O  PB5
#define		JOYSTICK_HELM	23	// I  PC0
#define		JOYSTICK_WIND	24	// I  PC1
#define 	SIPPUFF_HELM	25	// I  PC2
#define		SIPPUFF_WIND	26	// I  PC3
#define 	BATTERY    	27	// I  PC4

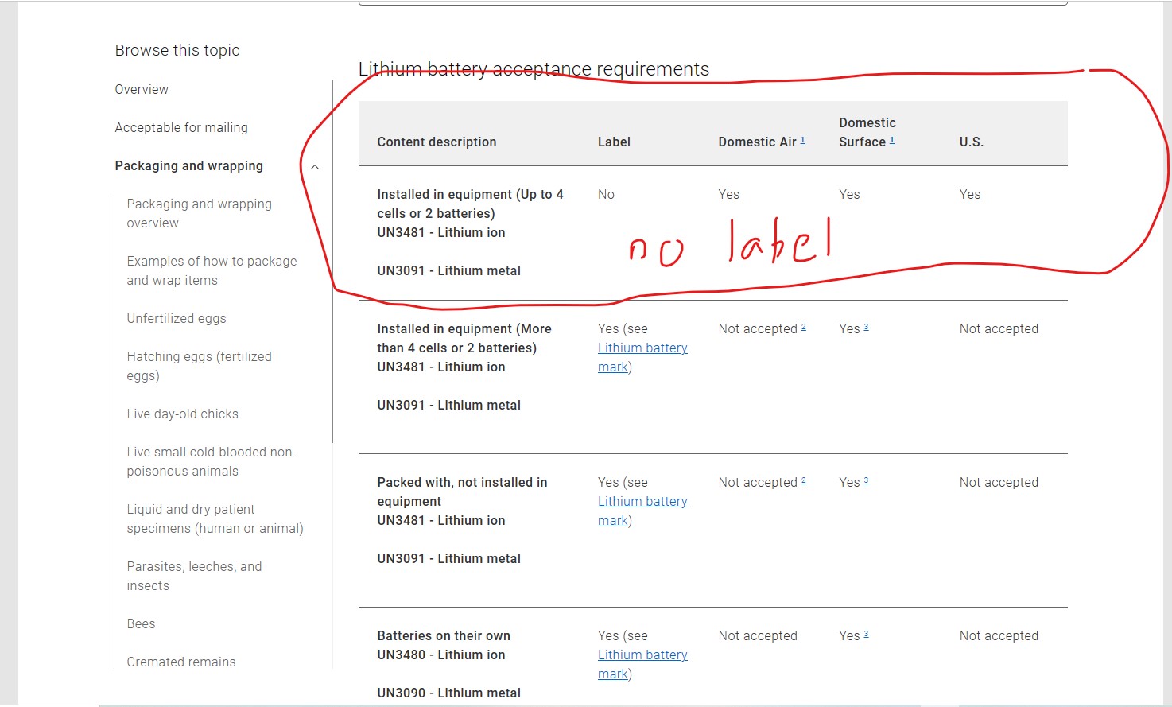
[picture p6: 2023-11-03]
manufacturing info/Canada Post lithium battery shipping requirements 2023.jpg

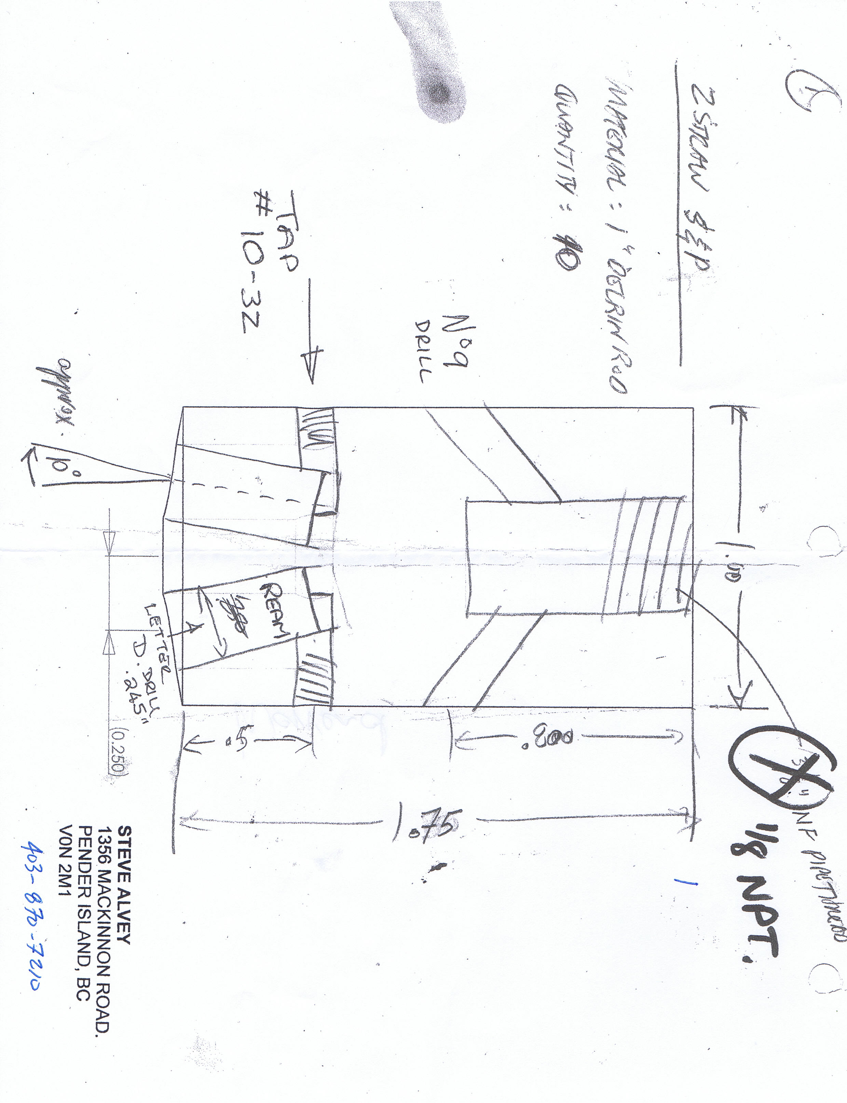
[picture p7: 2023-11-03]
module design files/sip&puff/S&P stalk delrin mouth boss - Copy.jpg

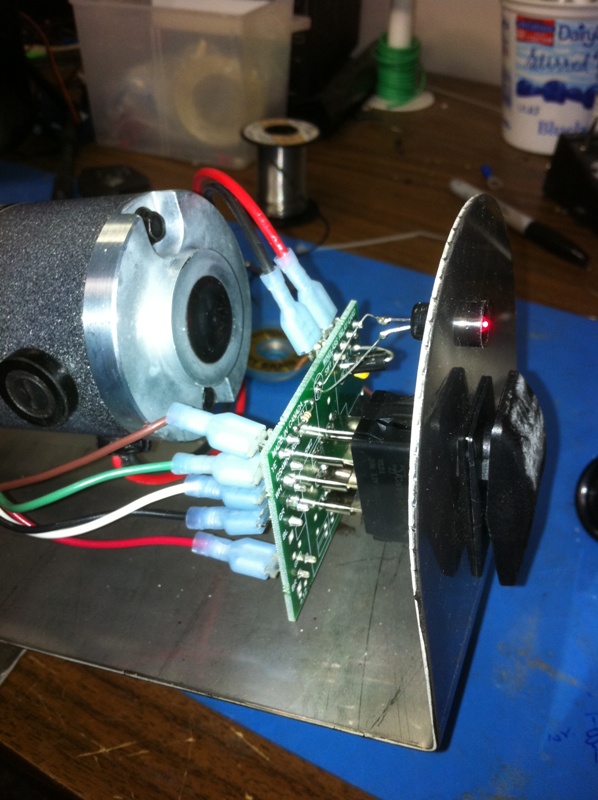
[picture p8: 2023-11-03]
module design files/windlass/Windlass PCB photos/Mk II Windlass PCB.JPG

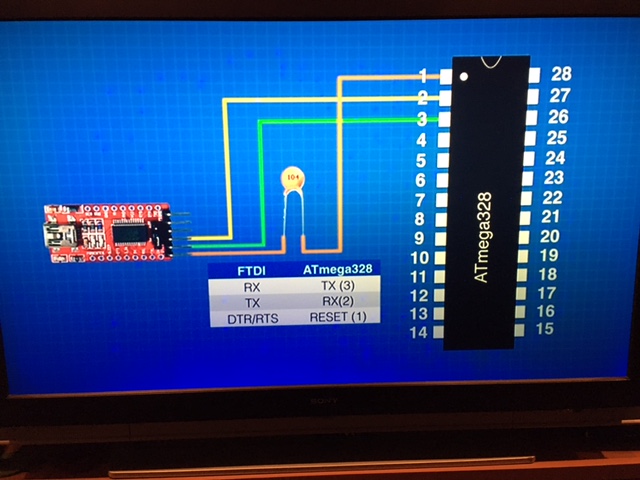
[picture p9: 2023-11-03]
module design files/joystick/Arduino_MKVI development/Arduino_development/Arduino connection for USB TTL converter.JPG

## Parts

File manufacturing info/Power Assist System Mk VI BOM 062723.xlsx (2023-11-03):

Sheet: Mk VI Modules - BOM
 |  |  |  |  |  |  |  | 50 | 100 | 200
 |  |  |  |  |  | AMPCO Quote 11/02/2018 | top overlay | $20.67 | $17.87 | $16.50
Bills of Material - Modules and Assemblies |  |  |  | 2023-03-06 |  |  | side | $7.84 | $5.84 | $4.84
 |  |  |  |  |  |  | warning label | $6.29 | $4.49 | $3.59
 |  | #REF! |  |  |  |  | 50 sets: | $2132.00 | + tax and ship | unit cost | $52.53
000 | A | Pelican Case 1610 | shipping case with wheels | top | Optimal Cases & Lights | Pelican 1610 Protector Case with foam insert | $546.25 |  | $54.62 | 1 | $600.88
Mk VI Arduino Joystick Module |  |  |  |  |  |  |  | 1.39
Part # | Assem | Name | Description | Location | Vendor | Vendor Part # | Cost CDN | Cost US | shipping | Quan | Total cost
100 | J | Enclosure | NEMA 4 fiberglass box | top | Electrosonic | R132-104-000 | $105.00 |  | $10.50 | 1 | $115.50
101 | J | DSA MKV REVB PCB | Arduino PIC PCB including S&P | inside | Alvey | DSAMKVI (REV C) PCB | $255.18 |  | $0.00 | 1 | $255.18
102 | J | Power Assist labeling | chassis overlays (3 parts: A,B,C) | top | Ampco | 99003-04 & 05 | $55.00 |  | $5.50 | 1 | $60.50
103 | J | Joystick - switched | SUZO HAPP 4 WAY JOYSTICK PSM-30 W/.250" SWITCH BLACK | top | Suzo-Happ | 50-0155-00 |  | $22.75 | $32.00 | 1 | $63.62
104 | J | Fastener for joystick | M4 x 20mm hex head SS screw | joystick | McMaster Carr | 94500A283 |  | $0.10 | $0.01 | 4 | $0.60
105 | J | Fastener for joystick | M4 hex head SS nut | joystick | McMaster Carr | 91828A231 |  | $0.10 | $0.01 | 4 | $0.60
106 | J | EV-100 Helm Drive Connector | Bulgin 3-pin female- chassis mount | back | Allied Electronics | Aliied 70099239 PX-0730/S | $32.00 |  | $3.20 | 1 | $35.20
107 | J | power cord | 48" long 5 (or 6) 16 GA conductor cable | chassis | B&E Electronincs |  | $15.00 |  | $1.50 | 1 | $16.50
108 | J | power cord connector | Bulgin 6-pin male cable connector | back | Allied Electronics | Allied 70099206 PX-0739/P | $38.00 |  | $3.80 | 1 | $41.80
109 | J | connector dust cap | Bulgin dust cap | back | Allied Electronics | Allied 70099262 PX-0733 | $3.00 |  | $0.30 | 1 | $3.30
110 | J | Fastener for PCB | M4 x 5mm hex head SS screw | chassis | McMaster Carr | 94500A281 |  | $0.10 | $0.01 | 4 | $0.60
111 | J | power cord grip | strain relief grip for power cord | chassis | McMaster Carr | 69915K54 |  | $3.24 | $0.32 | 1 | $4.83
112 | J | anti-skid pads | 1/4" adhesive-backed rubber pads | bottom | from EarthX Batteries | surplus from each battery | $0.00 |  | $0.00 | 2 | $0.00
113 | J | J11 - rudder drive harness | J11 - rudder drive harness | inside | Alvey |  | $3.00 |  | $0.30 | 1 | $3.30
197 | J | Assembly |  |  | IML |  |  |  | $0.00 | 1 | $0.00
198 | J | Mark-up |  |  |  |  |  |  | $0.00 | 1 | $0.00
199 | J | Manufacturing Cost - Mk VI Joystick Module |  |  |  |  |  |  | $57.454 |  | $601.52
 |  | Mk VI Development costs - amortization
 |  | Total Cost base - Mk VI Joystick Module |  |  |  |  |  |  |  |  | $601.5211
 |  | Published Retail Price |  |  |  |  |  |  | US $ 1,395 |  | $1675
Mk V Joystick Module (Switched joystick) |  |  |  |  |  |  |  | 1.39
Part # | Assem | Name | Description | Location | Vendor | Vendor Part # | Cost CDN | Cost US | shipping | Quan | Total cost
100 | J | Enclosure | NEMA 4 fiberglass box | top | Electrosonic | R132-104-000 | $105.00 |  | $10.50 | 1 | $115.50
101 | J | DSA MKV REVB PCB | integration & S&P PCB | inside | Alvey | DSAMKV (REV x) PCB | $280.46 |  | $0.00 | 1 | $280.46
102 | J | Sabretooth 2x32A (Dimension Engineering) | Dual PWM Controller (brushed DC) | internal | Robot Shop.com | RB-DIM-47 | $150.00 |  | $15.00 | 1 | $165.00
103 | J | Power Assist labeling | chassis overlays (3 parts: A,B,C) | top | Ampco | 99003-04 & 05 | $55.00 |  | $5.50 | 1 | $60.50
104 | J | Joystick - switched | SUZO HAPP 4 WAY JOYSTICK PSM-30 W/.250" SWITCH BLACK | top | Suzo-Happ | 50-0155-00 |  | $22.75 | $32.00 | 1 | $63.62
105 | J | Fastener for joystick | M4 x 20mm hex head SS screw | joystick | McMaster Carr | 94500A283 |  | $0.10 | $0.01 | 4 | $0.60
106 | J | Fastener for joystick | M4 hex head SS nut | joystick | McMaster Carr | 91828A231 |  | $0.10 | $0.01 | 4 | $0.60
107 | J | EV-100 Helm Drive Connector | Bulgin 3-pin female- chassis mount | back | Allied Electronics | Aliied 70099239 PX-0730/S | $32.00 |  | $3.20 | 1 | $35.20
108 | J | power cord | 48" long 5 (or 6) 16 GA conductor cable | chassis | B&E Electronincs |  | $15.00 |  | $1.50 | 1 | $16.50
109 | J | power cord connector | Bulgin 6-pin male cable connector | back | Allied Electronics | Allied 70099206 PX-0739/P | $38.00 |  | $3.80 | 1 | $41.80
110 | J | connector dust cap | Bulgin dust cap | back | Allied Electronics | Allied 70099262 PX-0733 | $3.00 |  | $0.30 | 1 | $3.30
111 | J | Fastener for PCB | M4 x 5mm hex head SS screw | chassis | McMaster Carr | 94500A281 |  | $0.10 | $0.01 | 4 | $0.60
112 | J | power cord grip | strain relief grip for power cord | chassis | McMaster Carr | 69915K54 |  | $3.24 | $0.32 | 1 | $4.83
113 | J | anti-skid pads | 1/4" adhesive-backed rubber pads | bottom | from EarthX Batteries | surplus from each battery | $0.00 |  | $0.00 | 2 | $0.00
114 | J | J11 - rudder drive harness | J11 - rudder drive harness | inside | Alvey |  | $3.00 |  | $0.30 | 1 | $3.30
197 | J | Assembly |  |  | IML |  |  |  | $0.00 | 1 | $0.00
198 | J | Mark-up |  |  |  |  |  |  | $0.00 | 1 | $0.00
199 | J | Manufacturing Cost - Mk V Joystick Module |  |  |  |  |  |  | $72.454 |  | $791.79
 |  | Mk V Development costs - amortization
 |  | Total Cost base - Mk V Joystick Module |  |  |  |  |  |  |  |  | $791.7941
 |  | Published Retail Price |  |  |  |  |  |  | US $ 1,395 |  | $1675
Martin 16 Power Assist subassemblies |  |  |  |  |  | 0.245
Part # | Assem | Name | Description | Location | Vendor | Vendor Part # | Cost CDN | Cost US | shipping | Quan | Total cost
200 | S | helm linear actuator | EV-100 tiller drive | EV-100 | Binnacle.com | Q047 | $1253.50 | $0.00 | $125.35 | 1 | $1378.85
201 | S | helm linear actuator - connector | Bulgin 3-pin male cable | EV-100 | Allied Electronics | Allied 70099204 PX-0731/P | $38.00 |  | $3.80 | 1 | $41.80
202 | S | helm linear actuator - power cord | 2 conductor 18GA insulated cable - 42" | EV-100 | McMaster Carr | 7082K26 | $5.00 |  | $0.50 | 1 | $5.50
203 | S | drive pedestal | EV-100 pedestal mount | Martin 16 | Steveston Marine | D030 | $99.00 |  | $9.90 | 1 | $108.90
204 | S | pushrod | 54" long x .375" O.D. SS tube (custom) | Martin 16 | Aerotech Specialty Welding | SS RD TUBE SMLS 304 .375 x .049 wall | $100.00 |  | $10.00 | 1 | $110.00

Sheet: PCB - BOM
 |  |  |  |  |  |  |  | 2018-11-04 |  | Steve Alvey 403-870-7210
Inventory | Value |  | Bills of Material - PCBs
 |  |  | Mk VI PCB (Arduino architecture; introduced June 2021) |  |  |  |  |  |  |  |  |  |  | Exchange |  |  | Prod Run | 6
GST | $169.58 |  |  |  | 77 |  |  |  |  |  |  |  |  | 1.42
 | $3391.54 |  | Component # | Assem | Quan | Vendor Part # | Description | Name | Location | Vendor | Lead time | Pur/Fab | Cost CDN | Cost US | shipping | Total cost | Required | On-Hand | Order | Name | Description | Vendor | Vendor Part # | Vendor Phone
 | $0.00 | 1 | PCB MKVI C | MKVI | 1 | DSAMVIC | 3 1/2" x 5" PCB | DSA MkVI Revision D PCB | PCB | JCLPCB | 3 | P |  | $15.00 | $1.50 | $21.00 | 6 | 0 | 6 | DSA MkVI Revision D PCB | 3 1/2" x 5" PCB | JCLPCB | DSAMVIC | 604-276-9717
 | $0.00 | 2 | U2 | MKVI | 1 | ATMEGA328-PU | ATMEGA 328-PU | Arduino PIC with bootloader | PCB | DigiKey | 1 | P |  | $5.00 | $0.50 | $7.00 | 6 | 0 | 6 | Arduino PIC with bootloader | ATMEGA 328-PU | DigiKey | ATMEGA328-PU | 800-344-4539
 | $0.00 | 3 | U1, U5 | MKVI | 2 | MPXV7007GC6U-ND (https://www.digikey.ca/product-detail/en/nxp-usa-inc/MPXV7007GC6U/MPXV7007GC6U-ND/1168440) | PRESSURE SENSOR AXIAL PORT 8-SOP | pnuematic sensor | PCB | DigiKey | 1 | P | $48.00 |  | $1.00 | $98.00 | 12 | 0 | 12 | pnuematic sensor | PRESSURE SENSOR AXIAL PORT 8-SOP | DigiKey | MPXV7007GC6U-ND | 954-788-3611 | 555 SW 12 Ave, 204, Pompano Beach FL 33069
 | $0.00 | 4 | U3 | MKVI | 1 | ULN2003AIN | Darlington transistor array (7) | relay / LED drivers | PCB | DigiKey | 1 | P | $1.50 |  | $0.15 | $1.65 | 6 | 0 | 6 | relay / LED drivers | Darlington transistor array (7) | DigiKey | ULN2003AIN | 800-344-4539
 | $0.00 | 5 | U4 | MKVI | 1 | NJM7805FA-ND | NJR Corp 5v - 1A Voltage regulator | +5V power regulator | PCB | DigiKey | 1 | P | $1.50 |  | $0.15 | $1.65 | 6 | 0 | 6 | +5V power regulator | NJR Corp 5v - 1A Voltage regulator | DigiKey | NJM7805FA-ND | 800-344-4539
 | $0.00 | 6 | U6 | MKVI | 1 | MD13S | Cytron MD13S PWM module | 13A PWM Module | PCB | Cytron | 1 | P |  | $20.00 | $2.00 | $28.00 | 6 | 0 | 6 | 13A PWM Module | Cytron MD13S PWM module | Cytron | MD13S | 800-344-4539
 | $0.00 | 7 | X2 | MKVI | 1 | 61-221-0 | Minature PC mount buzzer (Projects Unlimited) | Buzzer | PCB | Banggood | 1 | P | $2.21 |  | $0.22 | $2.43 | 6 | 0 | 6 | Buzzer | Minature PC mount buzzer (Projects Unlimited) | Banggood | 61-221-0 | 800-344-4539
 | $0.00 | 8 | X1 | MKVI | 1 | 2151-AS-16.000-20-EXT-ND | 16MHz crystal - low profile | PIC oscillator | PCB | DigiKey | 1 | P | $1.50 |  | $0.15 | $1.65 | 6 | 0 | 6 | PIC oscillator | 16MHz crystal - low profile | DigiKey | 2151-AS-16.000-20-EXT-ND | 800-344-4539
 | $0.00 | 9 | K2 | MKVI | 1 | Z2307-ND | OMRON G2R-1A-E 2068W1 12V/16A | main power relay - reverse polarity protect | PCB | DigiKey | 2 | P | $9.75 |  | $0.98 | $10.72 | 6 | 0 | 6 | main power relay - reverse polarity protect | #REF! | DigiKey | OMRON G2R-1A-E 2068W1 12V/16A
 | $0.00 | 10 | C7, C8 | MKVI | 2 |  | 22pF ceramic capacitor | resonator |  | Banggood | 1 | P |  | $0.25 | $0.03 | $0.70 | 12 | 0 | 12 | resonator | 22pF ceramic capacitor | Banggood | 0 | 800-344-4539
 | $0.00 | 11 | C9 | MKVI | 1 | P5142-ND | 1000 microfarad ELECTROLYTIC (16V) cap | +12V power supply | PCB | DigiKey | 1 | P | $1.00 |  | $0.10 | $1.10 | 6 | 0 | 6 | +12V power supply | 1000 microfarad ELECTROLYTIC (16V) cap | DigiKey | P5142-ND | 800-344-4539
 | $0.00 | 12 | C10, C11 | MKVI | 2 | P2038-ND | 10 microfarad ELECTROLYTIC (16V) cap | +12V power supply | PCB | DigiKey | 1 | P | $1.50 |  | $0.15 | $3.30 | 12 | 0 | 12 | +12V power supply | 10 microfarad ELECTROLYTIC (16V) cap | DigiKey | P2038-ND | 800-344-4539
 | $0.00 | 13 | C12, C13, C15, C16, C17, C18 | MKVI | 6 | 399-4309-ND | 0.47 microfarad ceramic cap (50V) | by-pass | top | DigiKey | 1 | P | $0.60 |  | $0.06 | $3.96 | 0 |  |  | 0 | by-pass | 0.47 microfarad ceramic cap (50V) | DigiKey | 399-4309-ND | 800-344-4539 | $0.60 | $0.00 | $0.06 | #VALUE!
 | $0.00 | 14 | C14 | MKVI | 1 |  | 4.7 nanofarad ceramic cap (50V) | V sense resistor bridge by-pass | top | DigiKey | 1 | P | $1.25 |  | $0.12 | $1.38 | 0 |  |  | 0 | V sense resistor bridge by-pass | 4.7 nanofarad ceramic cap (50V) | DigiKey | 0 | 800-344-4539 | $1.25 | $0.00 | $0.12 | #VALUE!
 | $0.00 | 15 | C19 | MKVI | 1 | P4944-ND | .1uF ceramic cap (50V) | Arduino reset line | top | DigiKey | 1 | P | $1.22 |  | $0.12 | $1.34 | 0 |  |  | 0 | Arduino reset line | .1uF ceramic cap (50V) | DigiKey | P4944-ND | 800-344-4539 | $1.22 | $0.00 | $0.12 | #VALUE!
 | $0.00 | 16 | F1 | MKVI | 1 | 18-AHRL 1400-ND | 14A PTC | Polythermal current limiter - 14A | PCB | DigiKey | 1 | P | $2.50 |  | $0.25 | $2.75 | 6 | 0 | 6 | Polythermal current limiter - 14A | 14A PTC | DigiKey | 18-AHRL 1400-ND | 800-344-4539
 | $0.00 | 17 | D8, D7 | MKVI | 2 | 1N4001GP-E3/73 | power diode | reverse polarity protect - main power relay | PCB | DigiKey | 1 | P | $0.75 |  | $0.08 | $1.65 | 12 | 0 | 12 | reverse polarity protect - main power relay | power diode | DigiKey | 1N4001GP-E3/73 | 800-344-4539
 | $0.00 | 18 | D1, D9, D10, D11 | MKVI | 4 | 497-2512-1-ND | BAT48 40V schotky diode | reverse polarity protection | PCB | DigiKey | 1 | P | $0.50 |  | $0.05 | $2.20 | 24 | 0 | 24 | reverse polarity protection | BAT48 40V schotky diode | DigiKey | 497-2512-1-ND | 800-344-4539
 | $0.00 | 19 | D2, D3, D4, D5, D6, D12 | MKVI | 6 | XLM2MR12W | high brightness RED LED (30mA) pg 583 | indicator LEDs | PCB | DigiKey | 1 | P | $1.10 |  | $0.11 | $7.26 | 36 | 0 | 36 | indicator LEDs | high brightness RED LED (30mA) pg 583 | DigiKey | XLM2MR12W | 800-344-4539
 | $0.00 | 20 | R1 | MKVI | 1 | 470QBK-ND‎ | 470R - 5% 1/4 W resistor | Windlass LED shunt | PCB | DigiKey | 1 | P | $0.10 |  | $0.10 | $0.20 | 6 | 0 | 6 | Windlass LED shunt | 470R - 5% 1/4 W resistor | DigiKey | 470QBK-ND‎ | 800-344-4539
 | $0.00 | 21 | R3 | MKVI | 1 | 4.99KXBK-ND | 4.99K - 1% 1/8 W resistor | VOLTAGE REF | PCB | DigiKey | 1 | P | $0.40 |  | $0.10 | $0.50 | 6 | 0 | 6 | VOLTAGE REF | 4.99K - 1% 1/8 W resistor | DigiKey | 4.99KXBK-ND | 800-344-4539
 | $0.00 | 22 | R4 | MKVI | 1 | 1KEBK-ND | 1K - 5% 1/8 W resistor | LED resistor | PCB | DigiKey | 1 | P | $0.10 |  | $0.01 | $0.11 | 6 | 0 | 6 | LED resistor | 1K - 5% 1/8 W resistor | DigiKey | 1KEBK-ND | 800-344-4539
 | $0.00 | 23 | R5 | MKVI | 1 | 11.0KXBK-ND | 11.0K - 1% 1/8 W resistor | VOLTAGE REF | PCB | DigiKey | 1 | P | $0.40 |  | $0.10 | $0.50 | 6 | 0 | 6 | VOLTAGE REF | 11.0K - 1% 1/8 W resistor | DigiKey | 11.0KXBK-ND | 800-344-4539
 | $0.00 | 24 | R6 | MKVI | 1 | 10KEBK-ND | 10K - 5% 1/8 W resistor | pull up for ULN2003 | PCB | DigiKey | 1 | P | $0.75 |  | $0.08 | $0.82 | 6 | 0 | 6 | pull up for ULN2003 | 10K - 5% 1/8 W resistor | DigiKey | 10KEBK-ND | 800-344-4539
 | $0.00 | 25 | RN1 | MKVI | 1 | 4306R-101-471LF-ND | 6 pin SIP 470R - 1% 1/4 W resistor | R for LEDs | PCB | DigiKey | 1 | P | $1.90 |  | $0.19 | $2.09 | 6 | 0 | 6 | R for LEDs | 6 pin SIP 470R - 1% 1/4 W resistor | DigiKey | 4306R-101-471LF-ND | 800-344-4539
 | $0.00 | 26 | RN2, RN3 | MKVI | 1 | 4610X-101-103LF-ND | 10 pin SIP 10K - 1% 1/4 W resistor | various R | PCB | DigiKey | 1 | P | $0.75 |  | $0.08 | $0.82 | 6 | 0 | 6 | various R | #REF! | DigiKey | #REF! | 800-344-4539
 | $0.00 | 27 | RN4, RN5 | MKVI | 2 | 4606X-101-104LF ?? | 100K x 5 1% 1/8 W SIP | 100K for joystick and S&P sensors reference | PCB | DigiKey | 1 | P | $1.20 |  | $0.10 | $2.60 | 12 | 0 | 12 | 100K for joystick and S&P sensors reference | 100K x 5 1% 1/8 W SIP | DigiKey | 4606X-101-104LF ?? | 800-344-4539
 | $0.00 | 28 | SW2 | MKVI | 1 |  | PCB mount - pushbutton switch | program mode switch | PCB | Banggood | 1 | P |  | $0.25 | $0.03 | $0.35 | 6 | 0 | 6 | program mode switch | PCB mount - pushbutton switch | Banggood | 0 | 800-344-4539
 | $0.00 | 29 | J1 | MKVI | 1 | WM4203-ND | .100 5-pin stick header - locking | analog joystick | PCB | DigiKey | 1 | P | $0.40 |  | $0.04 | $0.44 | 6 | 0 | 6 | analog joystick | .100 5-pin stick header - locking | DigiKey | WM4203-ND | 800-344-4539
 | $0.00 | 30 | J2 | MKVI | 1 | 277-1065-ND | .200 Euroconnector - 5-pin - PLUG | Power cord connector | PCB | DigiKey | 1 | P | $9.50 |  | $0.95 | $10.45 | 6 | 0 | 6 | #REF! | .200 Euroconnector - 5-pin - PLUG | DigiKey | 277-1065-ND | 800-344-4539
 | $0.00 | 31 | J2 | MKVI | 1 | 277-1153-ND | .200 Euroconnector - 5-pin - PCB header | Power cord connector socket PCB | PCB | DigiKey | 1 | P | $3.50 |  | $0.35 | $3.85 | 6 | 0 | 6 | Power cord connector | #REF! | DigiKey | 277-1153-ND | 800-344-4539
 | $0.00 | 32 | J2 | MKVI | 1 | 277-1062-ND | .200 Euroconnector - 2-pin - PLUG | helm drive connector | PCB | DigiKey | 1 | P | $4.50 |  | $0.45 | $4.95 | 6 | 0 | 6 | Power cord connector socket PCB | .200 Euroconnector - 2-pin - PCB header | DigiKey | 277-1062-ND | 800-344-4539
 | $0.00 | 33 | J2 | MKVI | 1 | 277-1150-ND | .200 Euroconnector - 2-pin - PCB header | helm drive connector | PCB | DigiKey | 1 | P | $1.50 |  | $0.15 | $1.65 | 6 | 0 | 6 | helm drive connector | .200 Euroconnector - 5-pin - PCB header | DigiKey | 277-1150-ND | 800-344-4539
 | $0.00 | 34 | J3 | MKVI | 1 | 28-3518-10T-ND | 28 pin socket for PIC | PIC socket | top | Banggood | 1 | P |  | $1.00 | $0.10 | $1.40 | 6 | 0 | 6 | PIC socket | 28 pin socket for PIC | Banggood | 28-3518-10T-ND | 800-344-4539
 | $0.00 | 35 | J4 | MKVI | 1 | HDR100IMP06F-G-V-ST | .100 6-pin FEMALE header | USB header (Arduino) | PCB | DigiKey | 1 | P | $0.40 |  | $0.04 | $0.44 | 6 | 0 | 6 | USB header (Arduino) | .100 6-pin FEMALE header | DigiKey | HDR100IMP06F-G-V-ST | 800-344-4539
 | $0.00 | 36 | J5, J6, DTR, CTS | MKVI | 4 | 900-0022032031-ND | .100 3-pin stick header | RC Receiver connector; JUMPERS | PCB | Banggood | 1 | P | $0.40 |  | $0.04 | $1.76 | 24 | 0 | 24 | RC Receiver connector; JUMPERS | .100 3-pin stick header | Banggood | 900-0022032031-ND | 800-344-4539
 | $0.00 | 37 | J7, J9 | MKVI | 1 |  | pads for Cytron MD13S |  |  |  |  | P |  |  | $0.00 | $0.00 | 6 | 0 | 6 | 0 | pads for Cytron MD13S | 0 | 0 | 800-344-4539
 | $0.00 | 38 | J27 | MKVI | 1 | 16-3518-10T-ND | 16 pin socket for ULN2003 | ULN2003 socket | top | Banggood | 1 | P |  | $1.00 | $0.10 | $1.40 | 6 | 0 | 6 | ULN2003 socket | 16 pin socket for ULN2003 | Banggood | 16-3518-10T-ND | 800-344-4539
 | $0.00 | 39 | J8A, B, C, D | MKVI | 4 |  | .100 3-pin stick header - locking | switched joystick | top | Banggood | 1 | P | $1.50 |  | $0.15 | $6.60 | 24 | 0 | 24 | switched joystick | .100 3-pin stick header - locking | Banggood | 0 | 800-344-4539
 | $0.00 | 40 | J10 - J11 | MKVI | 2 | WM4002-ND | .100 4-pin MALE header | S&P module connector | PCB | DigiKey | 1 | P | $0.90 |  | $0.09 | $1.98 | 12 | 0 | 12 | S&P module connector | .100 4-pin MALE header | DigiKey | WM4002-ND | 800-344-4539
 | $0.00 | 41 | J12 - J19 | MKVI | 8 | 298-10283-ND | .250 90 degree insulated crimp connector | flying lead spade connector for joystick | PCB | DigiKey | 1 | P | $0.90 |  | $0.09 | $7.92 | 48 | 0 | 48 | flying lead spade connector for joystick | .250 90 degree insulated crimp connector | DigiKey | 298-10283-ND | 800-344-4539
 | $0.00 | 42 | H1 | MKVI | 4 |  | 3mm threaded standoff post - 15mm | mounting hardware for Cytron MD13S | PCB | Robotshop | 1 | P | $1.50 |  | $0.15 | $6.60 | 24 | 0 | 24 | mounting hardware for Cytron MD13S | 3mm threaded standoff post - 15mm | Robotshop | 0 | 954-788-3611 | 555 SW 12 Ave, 204, Pompano Beach FL 33069
 |  |  |  | MKVI | 3 |  |  | Assembly/Test |  |  | 3 | F |  |  |  | $0.00
 |  |  |  | MKVI | 1 |  |  | Mark-up |  |  |  | F |  |  | $0.00 | $0.00
 |  |  |  | MKVI |  |  |  | Manufacturing Cost - Mk VI PCB |  |  |  |  |  |  |  | $255.183
 |  |  |  |  |  |  |  | Development costs - amortization |  |  |  |  |  |  |  | $0
 |  |  | Published List Price |  |  |  |  | Published Retail Price (including S&P sensors) |  |  |  |  |  |  |  | $500
 |  |  |  |  |  |  |  | Orders
 |  |  |  |  |  |  |  | Total Sales Value |  |  |  |  |  |  |  | $0
 | Martin 16 Power Assist System - Schedule B
 | I, Stephen Alvey, of INVENTURE MANAGEMENT LIMITED, attest that this inventory valuation is accurate in count and value, at the time of transfer to Kevin Penny, on or about November 12, 2018
 | Total value at date of transfer: $ 2,203.08
 | Signature:
 | Date:
Inventory | Value |  | Bills of Material - PCBs
 |  |  | Mk V PCB (introduced Oct 2018) |  |  |  |  |  |  |  |  |  |  | Exchange |  |  | Prod Run | 6
GST | $92.25 |  |  |  |  |  |  |  |  |  |  |  |  | 1.3
 | $1844.90 |  | Component # | Assem | Quan | Vendor Part # | Description | Name | Location | Vendor | Lead time | Pur/Fab | Cost CDN | Cost US | shipping | Total cost | Required | On-Hand | Order | Name | Description | Vendor | Vendor Part # | Vendor Phone
5 | $275.00 | 1A | PCB MKVA (OCT 2018) | MKV |  | DSAMVA | 3 1/2" x 5" PCB | DSA MkV Revision A PCB | PCB | Omni Circuit Boards | 3 | P | $50.00 |  | $5.00 | $0.00 | 0 | 5 | 0 | DSA MkV Revision A PCB | 3 1/2" x 5" PCB | Omni Circuit Boards | DSAMVA | 604-276-9717
10 | $638.00 | 1B | PCB MKVB (NOV 2018) | MKV | 1 | DSAMVB | 3 1/2" x 5" PCB | DSA MkV Revision B PCB | PCB | Omni Circuit Boards | 3 | P | $58.00 |  | $5.80 | $63.80 | 6 | 10 | 0 | DSA MkV Revision B PCB | 3 1/2" x 5" PCB | Omni Circuit Boards | DSAMVB | 604-276-9717
10 | $13.20 | 2 | C1 | MKV | 1 | P3104-ND | 0.1 microfarad polypropelene cap (64V) | motor drive suppressor cap | PCB | DigiKey | 1 | P | $1.20 |  | $0.12 | $1.32 | 6 | 10 | 0 | motor drive suppressor cap | 0.1 microfarad polypropelene cap (64V) | DigiKey | P3104-ND | 800-344-4539
10 | $6.60 | 3 | C9 | MKV | 1 | P5142-ND | 1000 microfarad ELECTROLYTIC (16V) cap | +12V power supply | PCB | DigiKey | 1 | P | $0.60 |  | $0.06 | $0.66 | 6 | 10 | 0 | +12V power supply | 1000 microfarad ELECTROLYTIC (16V) cap | DigiKey | P5142-ND | 800-344-4539
7 | $5.77 | 4 | U1 | MKV | 1 | LM4041DIZ-ADJ/NOPB-ND | LM4041 PRECISION VOLTAGE REF | +9V REF for Battery LED | PCB | DigiKey | 1 | P | $0.75 |  | $0.08 | $0.82 | 6 | 7 | 0 | +9V REF for Battery LED | LM4041 PRECISION VOLTAGE REF | DigiKey | LM4041DIZ-ADJ/NOPB-ND | 800-344-4539
10 | $13.20 | 5 | PTC1 | MKV | 1 | RGEF900HF-ND | 9A PTC | Polythermal current limiter - 9A | PCB | DigiKey | 1 | P | $1.20 |  | $0.12 | $1.32 | 6 | 10 | 0 | Polythermal current limiter - 9A | 9A PTC | DigiKey | RGEF900HF-ND | 800-344-4539
5 | $8.25 | 6 | PTC2 | MKV | 1 | RGEF1400HF-ND | 14A PTC | Polythermal current limiter - 14A | PCB | DigiKey | 1 | P | $1.50 |  | $0.15 | $1.65 | 6 | 5 | 1 | Polythermal current limiter - 14A | 14A PTC | DigiKey | RGEF1400HF-ND | 800-344-4539
20 | $6.60 | 7 | D6, D7 | MKV | 2 | 1N4007-E3/54GICT-ND | power diode | reverse polarity protect - main power relay | PCB | DigiKey | 1 | P | $0.30 |  | $0.03 | $0.66 | 12 | 20 | 0 | reverse polarity protect - main power relay | power diode | DigiKey | 1N4007-E3/54GICT-ND | 800-344-4539
20 | $44.22 | 8 | Z1 | MKV | 1 | SA20CADICT-ND | Zener diode – 20V 500W bi-directional | motor drive suppressor diode | PCB | DigiKey | 1 | P | $2.01 |  | $0.20 | $2.21 | 6 | 20 | 0 | motor drive suppressor diode | Zener diode – 20V 500W bi-directional | DigiKey | SA20CADICT-ND | 800-344-4539
20 | $11.00 | 9 | D9, D11, D12 | MKV | 3 | 497-2512-1-ND | BAT48 40V schotky diode | reverse polarity protection | PCB | DigiKey | 1 | P | $0.50 |  | $0.05 | $1.65 | 18 | 20 | 0 | reverse polarity protection | BAT48 40V schotky diode | DigiKey | 497-2512-1-ND | 800-344-4539
39 | $8.58 | 10 | D13, D14, D15, D16 | MKV | 4 | 1N4148MSCT-ND | signal diode | LED driver | PCB | DigiKey | 1 | P | $0.20 |  | $0.02 | $0.88 | 24 | 39 | 0 | LED driver | signal diode | DigiKey | 1N4148MSCT-ND | 800-344-4539
70 | $46.20 | 11 | LED1 - LED5 | MKV | 5 | XLM2MR12W | high brightness RED LED (30mA) pg 583 | indicator LEDs | PCB | DigiKey | 1 | P | $0.60 |  | $0.06 | $3.30 | 30 | 70 | 0 | indicator LEDs | high brightness RED LED (30mA) pg 583 | DigiKey | XLM2MR12W | 800-344-4539
5 | $49.00 | 13 | K1 | MKV | 1 | 817-FTR-P2CN010W1 | 10V DPDT reversing relay (20A) | DC motor drive relay | PCB | Mouser | 3 | P |  | $7.00 | $0.70 | $9.80 | 6 | 5 | 1 | DC motor drive relay | 10V DPDT reversing relay (20A) | Mouser | 817-FTR-P2CN010W1
5 | $26.12 | 15 | K2 | MKV | 1 | Z2307-ND | OMRON G2R-1A-E 2068W1 12V/16A | main power relay - reverse polarity protect | PCB | DigiKey | 2 | P | $4.75 |  | $0.48 | $5.22 | 6 | 5 | 1 | main power relay - reverse polarity protect | #REF! | DigiKey | OMRON G2R-1A-E 2068W1 12V/16A
10 | $1.10 | 16 | R9 | MKV | 1 | 47RQBK-ND | 47R - 5% 1/4 W resistor | relay coil resistor | PCB | DigiKey | 1 | P | $0.10 |  | $0.01 | $0.11 | 6 | 10 | 0 | relay coil resistor | 47R - 5% 1/4 W resistor | DigiKey | 47RQBK-ND | 800-344-4539
50 | $5.50 | 17 | R3, R4, R7, R8, R13, R17 | MKV | 6 | 1KEBK-ND | 1K - 5% 1/8 W resistor | LED resistor | PCB | DigiKey | 1 | P | $0.10 |  | $0.01 | $0.66 | 36 | 50 | 0 | LED resistor | 1K - 5% 1/8 W resistor | DigiKey | 1KEBK-ND | 800-344-4539
20 | $2.20 | 18 | R1, R2, R5, R10, R11, R12 | MKV | 6 | 10KEBK-ND | 10K - 5% 1/8 W resistor | joystick reference | PCB | DigiKey | 1 | P | $0.10 |  | $0.01 | $0.66 | 36 | 20 | 16 | joystick reference | 10K - 5% 1/8 W resistor | DigiKey | 10KEBK-ND | 800-344-4539
25 | $5.00 | 19B | R15A | MKV | 1 | 115KXBK-ND | 115K - 1% 1/4 W resistor (critical value) | Vref voltage divider REVB/C PCB | PCB | DigiKey | 1 | P | $0.10 |  | $0.10 | $0.20 | 6 | 25 | 0 | Vref voltage divider REVB/C PCB | 115K - 1% 1/4 W resistor (critical value) | DigiKey | 115KXBK-ND | 800-344-4539
25 | $5.00 | 19B | R15B | MKV | 1 | 118KXBK-ND | 118K - 1% 1/4 W resistor (critical value) | Vref voltage divider REVB/C PCB | PCB | DigiKey | 1 | P | $0.10 |  | $0.10 | $0.20 | 6 | 25 | 0 | Vref voltage divider REVB/C PCB | 118K - 1% 1/4 W resistor (critical value) | DigiKey | 118KXBK-ND | 800-344-4539
25 | $5.00 | 19C | R14 | MKV | 1 | 1.00MXBK-ND | 1M - 1% 1/4 W resistor (critical value) | Vref voltage divider REVB/C PCB | PCB | DigiKey | 1 | P | $0.10 |  | $0.10 | $0.20 | 6 | 25 | 0 | Vref voltage divider REVB/C PCB | 1M - 1% 1/4 W resistor (critical value) | DigiKey | 1.00MXBK-ND | 800-344-4539
 | $0.00 | 21 | R16 | MKV | 1 | 1.2KEBK-ND | 1.2K - 5% 1/8 W resistor | BATTERY LED; REVB/C PCB | PCB | DigiKey | 1 | P | $0.10 |  | $0.10 | $0.20 | 6 | 0 | 6 | BATTERY LED; REVB/C PCB | 1.2K - 5% 1/8 W resistor | DigiKey | 1.2KEBK-ND | 800-344-4539
30 | $13.20 | 23 | RC RX | MKV | 3 | 900-0022032031-ND | .100 3-pin stick header | RC Receiver connector | PCB | DigiKey | 1 | P | $0.40 |  | $0.04 | $1.32 | 18 | 30 | 0 | RC Receiver connector | .100 3-pin stick header | DigiKey | 900-0022032031-ND | 800-344-4539
40 | $15.40 | 24 | JMP1, JMP2, JMP3 | MKV | 3 | WM4000-ND | .100 2-pin stick header | Jumpers for RELAY mode | PCB | DigiKey | 1 | P | $0.35 |  | $0.03 | $1.15 | 18 | 40 | 0 | Jumpers for RELAY mode | .100 2-pin stick header | DigiKey | WM4000-ND | 800-344-4539
10 | $25.30 | 25 | J2 | MKV | 1 | 277-1065-ND | .200 Euroconnector - 5-pin - PCB header | Power cord connector | PCB | DigiKey | 1 | P | $2.30 |  | $0.23 | $2.53 | 6 | 10 | 0 | Power cord connector | .200 Euroconnector - 5-pin - PCB header | DigiKey | 277-1065-ND | 800-344-4539
5 | $41.25 | 26 | J2 | MKV | 1 | 277-1153-ND | .200 Euroconnector - 5-pin - term block PLUG | Power cord connector | PCB | DigiKey | 1 | P | $7.50 |  | $0.75 | $8.25 | 6 | 5 | 1 | Power cord connector | .200 Euroconnector - 5-pin - term block PLUG | DigiKey | 277-1153-ND | 800-344-4539
5 | $8.25 | 27 | J3 | MKV | 1 | 277-1027-ND | .200 Euroconnector - 2-pin - PCB term block | Relay drive connector | PCB | DigiKey | 1 | P | $1.50 |  | $0.15 | $1.65 | 6 | 5 | 1 | Relay drive connector | .200 Euroconnector - 2-pin - PCB term block | DigiKey | 277-1027-ND | 800-344-4539
90 | $89.10 | 28 | J10 - J17 | MKV | 12 | 298-10283-ND | .250 90 degree insulated crimp connector | flying lead spade connector for joystick | PCB | DigiKey | 1 | P | $0.90 |  | $0.09 | $11.88 | 72 | 90 | 0 | flying lead spade connector for joystick | .250 90 degree insulated crimp connector | DigiKey | 298-10283-ND | 800-344-4539
50 | $27.50 | 29 | J30 - J33 | MKV | 4 |  | BLUE #10 ring crimp connector | ring connectors for Sabretooth module | PCB | DigiKey | 1 | P | $0.50 |  | $0.05 | $2.20 | 24 | 50 | 0 | ring connectors for Sabretooth module | BLUE #10 ring crimp connector | DigiKey | 0 | 800-344-4539
110 | $24.20 | 30 | J20 - J27 | MKV | 8 | 3548K-ND | Keystone .187 female spade | MPL switch PCB connector | PCB | DigiKey | 1 | P | $0.20 |  | $0.02 | $1.76 | 48 | 110 | 0 | MPL switch PCB connector | Keystone .187 female spade | DigiKey | 3548K-ND | 800-344-4539
 |  | 31 | S1, S2, S3, S4 | MKV |  | X05543 | MPL-502-range B micro switch | MPL pnuematic switch | PCB | Micro Pnuematic Logic Inc. 1-888-386-4270 | 1 | P |  | $40.00 | $4.00 | $0.00 | 0 | 0 | 0 | MPL pnuematic switch | MPL-502-range B micro switch | Micro Pnuematic Logic Inc. 1-888-386-4270 | X05543 | 954-788-3611 | 555 SW 12 Ave, 204, Pompano Beach FL 33069
30 | $16.50 | 32 | H1 | MKV | 4 | 14HTSP010 | 6-32 threaded standoff post - 1" | PCB mounting hardware | PCB | Quayle Electronics | 1 | P | $0.50 |  | $0.05 | $2.20 | 24 | 30 | 0 | PCB mounting hardware | 6-32 threaded standoff post - 1" | Quayle Electronics | 14HTSP010 | 954-788-3611 | 555 SW 12 Ave, 204, Pompano Beach FL 33069
30 | $4.95 | 33 | H2 | MKV | 4 | NYPS-632112 | 6-32 threaded screw - 1 1/2" | PCB mounting hardware | PCB | Quayle Electronics | 1 | P | $0.15 |  | $0.01 | $0.66 | 24 | 30 | 0 | PCB mounting hardware | 6-32 threaded screw - 1 1/2" | Quayle Electronics | NYPS-632112 | 954-788-3611 | 555 SW 12 Ave, 204, Pompano Beach FL 33069
40 | $6.60 | 34 | H3 | MKV | 4 | NYPS-63238 | 6-32 threaded screw - 3/8" | PCB mounting hardware | PCB | Quayle Electronics | 1 | P | $0.15 |  | $0.01 | $0.66 | 24 | 40 | 0 | PCB mounting hardware | 6-32 threaded screw - 3/8" | Quayle Electronics | NYPS-63238 | 954-788-3611 | 555 SW 12 Ave, 204, Pompano Beach FL 33069
40 | $6.60 | 35 | H4 | MKV | 4 | 14HTSP011 | 8-32 threaded stand-off post - 1/4" | PCB mounting hardware | PCB | Quayle Electronics | 1 | P | $0.15 |  | $0.01 | $0.66 | 24 | 40 | 0 | PCB mounting hardware | 8-32 threaded stand-off post - 1/4" | Quayle Electronics | 14HTSP011 | 954-788-3611 | 555 SW 12 Ave, 204, Pompano Beach FL 33069
 |  |  |  | MKV | 3 |  |  | Assembly/Test |  |  | 3 | F | $50.00 |  | $0.00 | $150.00
 |  |  |  | MKV | 1 |  |  | Mark-up |  |  |  | F |  |  | $0.00 | $0.00
 |  |  |  | MKV |  |  |  | Manufacturing Cost - Mk V PCB |  |  |  |  |  |  |  | $280.456
 |  |  |  |  |  |  |  | Development costs - amortization |  |  |  |  |  |  |  | $0
 |  |  | Published List Price |  |  |  |  | Published Retail Price |  |  |  |  |  |  |  | $300
 |  |  |  |  |  |  |  | Orders
 |  |  |  |  |  |  |  | Total Sales Value |  |  |  |  |  |  |  | $0
 |  |  | Windlass PCB REV C |  |  |  |  |  |  |  |  |  |  | Exchange |  |  | Prod Run | 6
 |  |  |  |  |  |  |  |  |  |  |  |  |  | 1.3
 | $55.00 |  | Component # | Assem | Quan | Vendor Part # | Description | Name | Location | Vendor | Lead time | Pur/Fab | Cost CDN | Cost US | shipping | Total cost | Required | On-Hand | Order | Name | Description | Vendor | Vendor Part # | Phone | Address
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

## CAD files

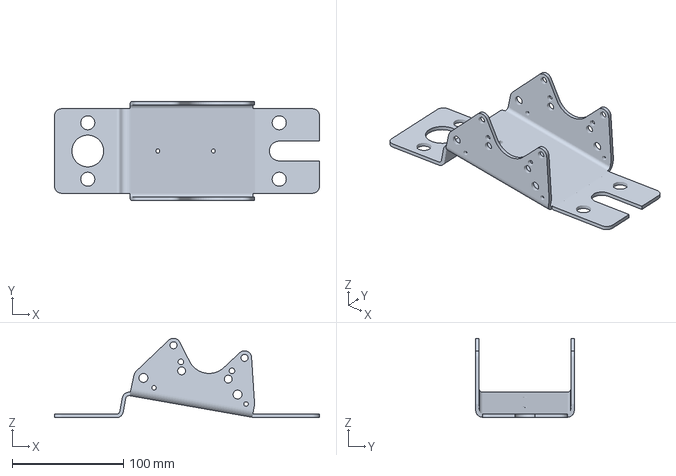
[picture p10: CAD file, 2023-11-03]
manufacturing info/3D printed parts/Windlass chassis V2 Base plate.3mf
238.7 x 88.9 x 71.6 mm

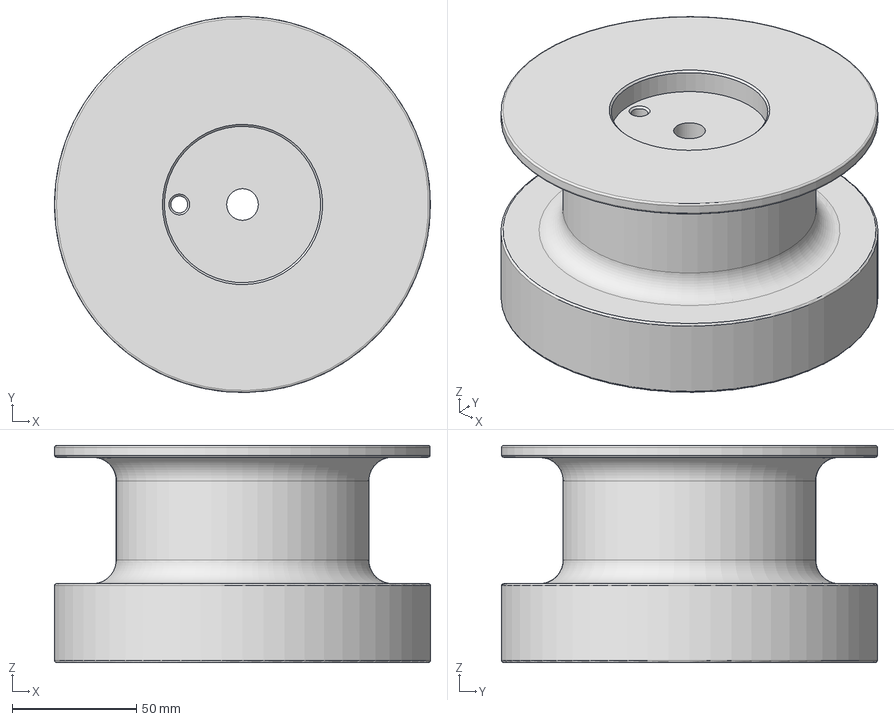
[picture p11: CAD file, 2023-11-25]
manufacturing info/Production CAD files/Windlass Drum CNC design v2.step
151.1 x 151.1 x 87.3 mm

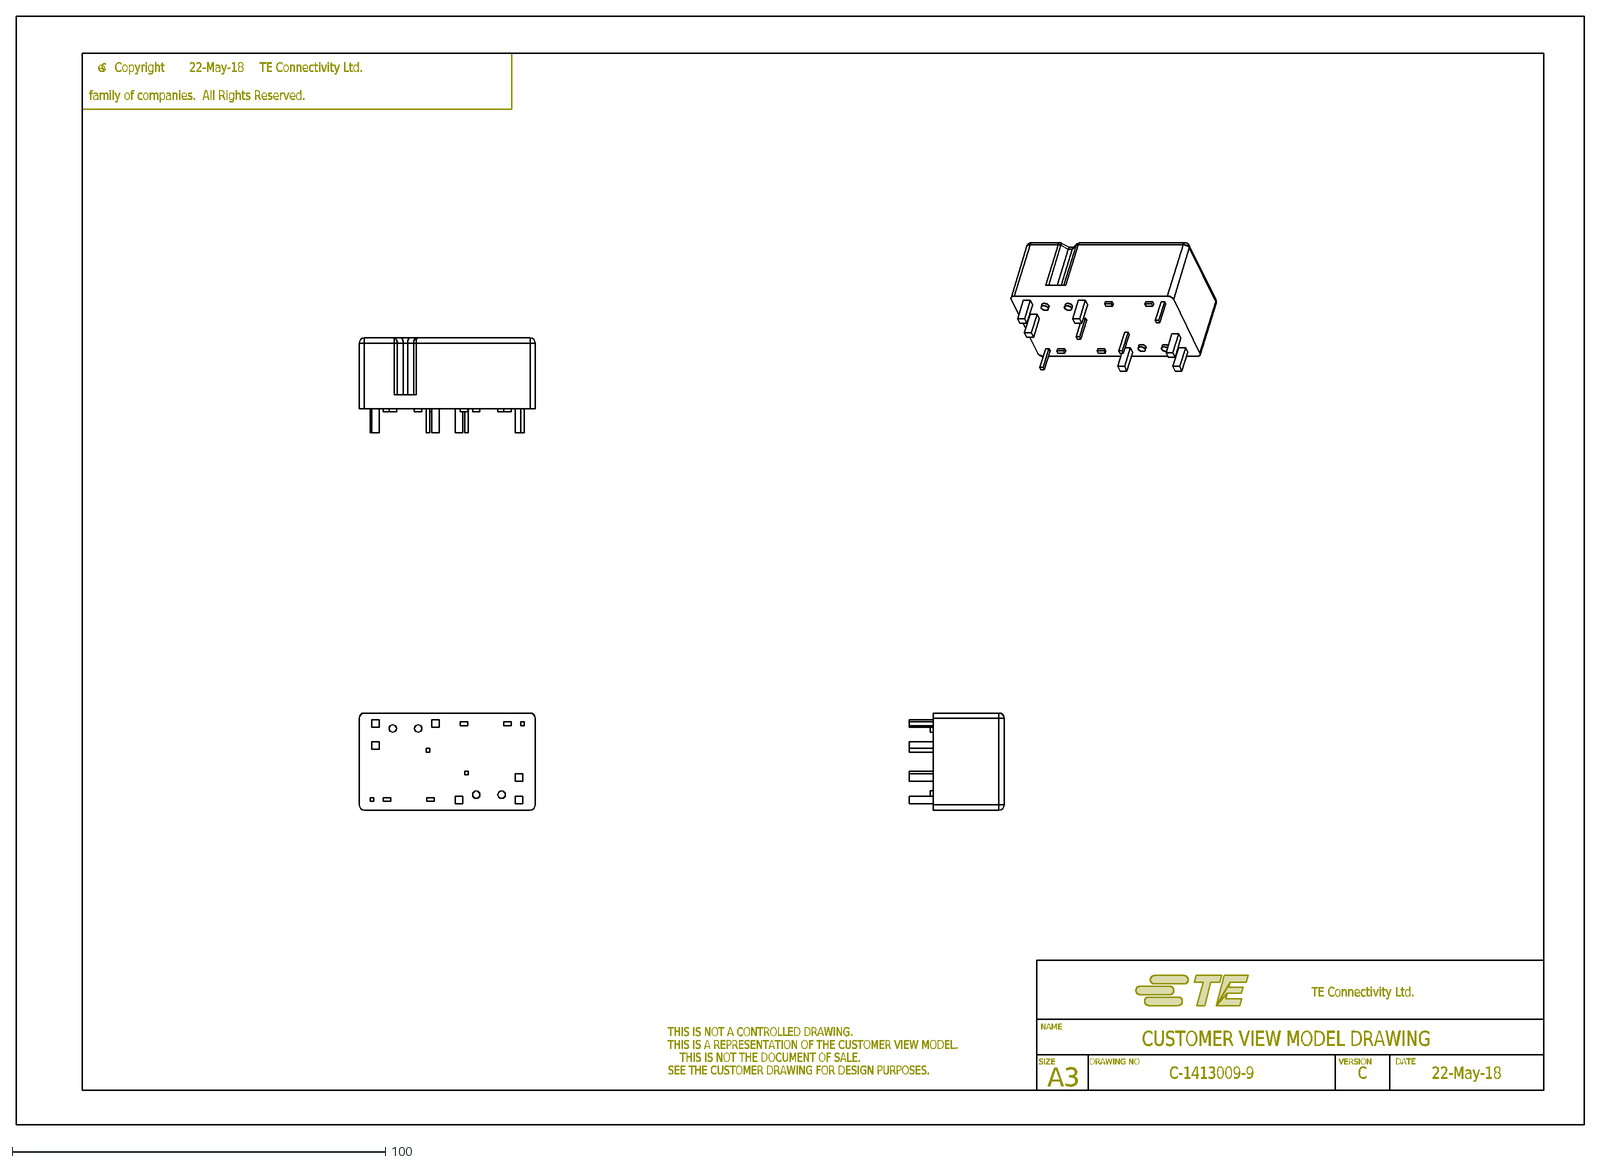
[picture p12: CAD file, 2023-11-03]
module design files/windlass/KiCAD PCB/c-1413009-9-c-2d.dxf
SIZE
DRAWING NO
VERSION
NAME
A3
CUSTOMER VIEW MODEL DRAWING
TE Connectivity Ltd.
DATE
THIS IS NOT A CONTROLLED DRAWING.
THIS IS A REPRESENTATION OF THE CUSTOMER VIEW MODEL.
THIS IS NOT THE DOCUMENT OF SALE.
SEE THE CUSTOMER DRAWING FOR DESIGN PURPOSES.
c
C-1413009-9
C
22-May-18
Copyright
family of companies. All Rights Reserved.

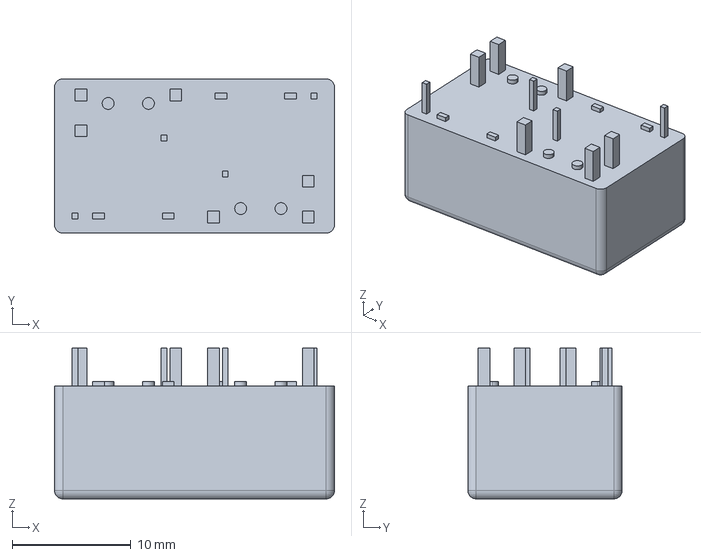
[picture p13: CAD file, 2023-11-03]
module design files/windlass/KiCAD PCB/V23086C2001A403/c-1413009-9-c-3d.igs
23.6 x 13.0 x 12.7 mm

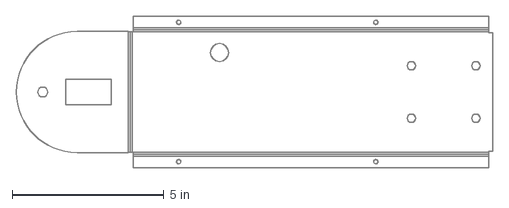
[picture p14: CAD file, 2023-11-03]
module design files/windlass/Windlass chassis V3 switch plate FINAL.dxf
15.7 x 4.99 in

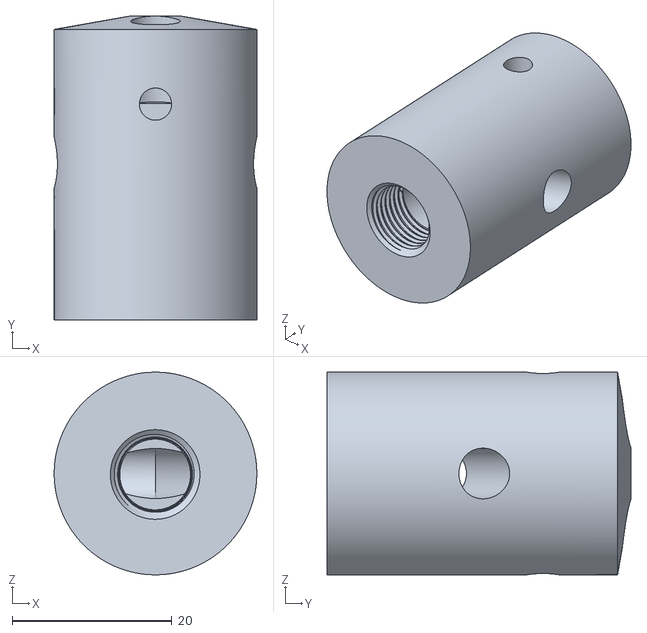
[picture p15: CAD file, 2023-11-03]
manufacturing info/3D printed parts/SnP straw boss.stl
25.4 x 38.1 x 25.4

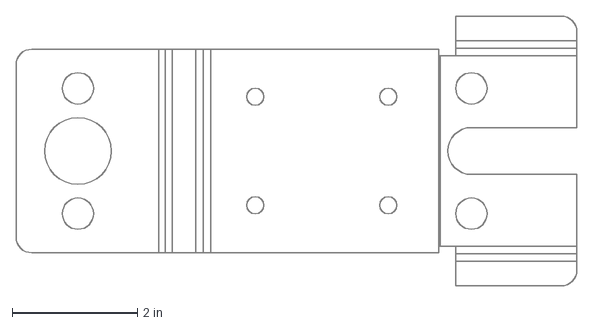
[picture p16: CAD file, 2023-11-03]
module design files/windlass/Windlass chassis V2 Base plate.dxf
8.95 x 4.31 in

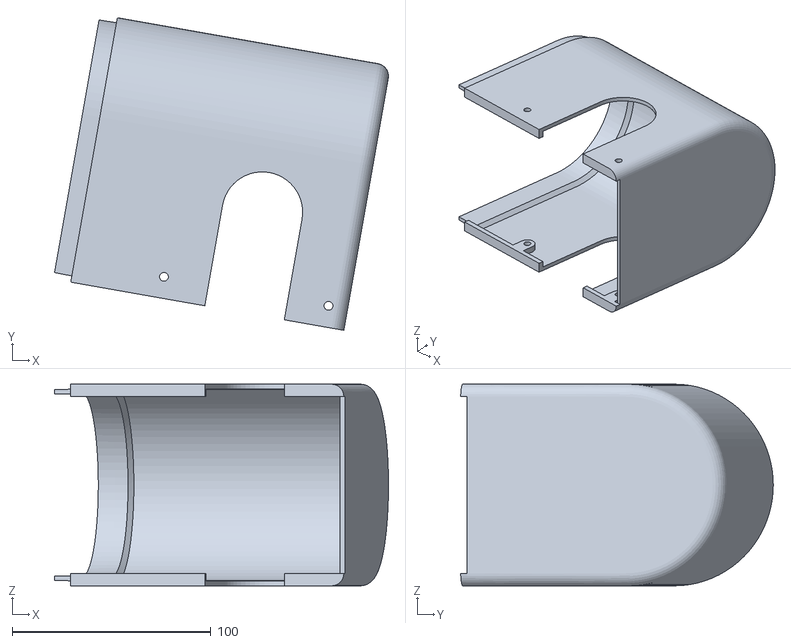
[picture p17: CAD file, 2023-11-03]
manufacturing info/3D printed parts/Windlass V2 v1.stl
168.2 x 157.5 x 101.6

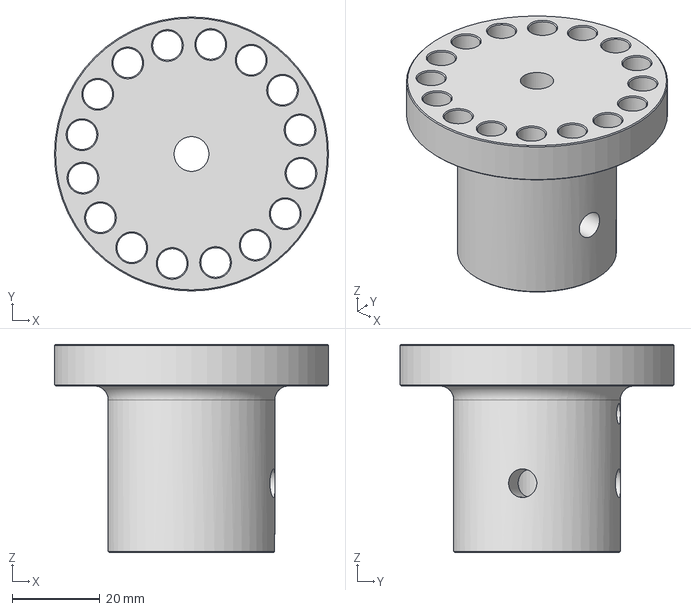
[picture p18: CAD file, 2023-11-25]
manufacturing info/Production CAD files/W209 - Windlass Hub PRODUCTION 14MM shaft.step
62.6 x 62.6 x 47.6 mm

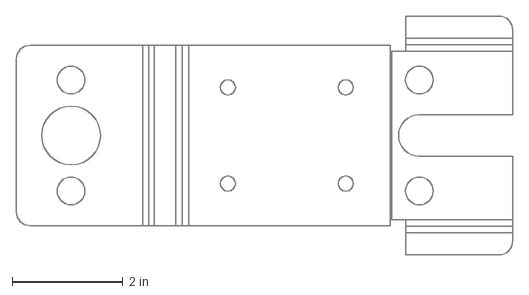
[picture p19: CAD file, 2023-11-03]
module design files/windlass/Windlass chassis V2 Base plate FINAL.dxf
8.95 x 4.31 in

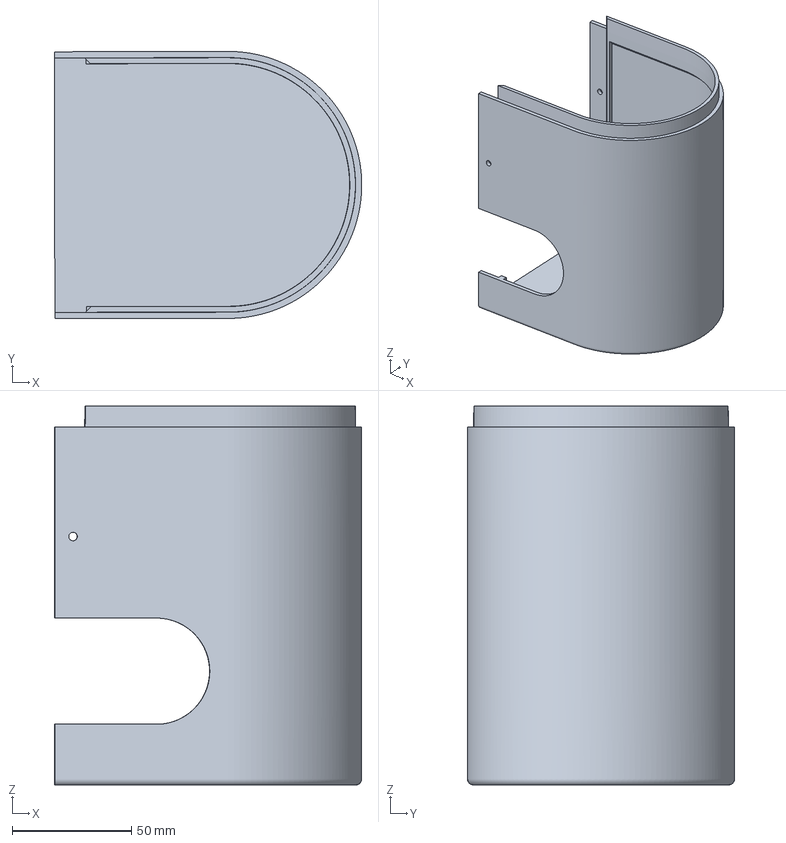
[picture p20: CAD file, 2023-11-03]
manufacturing info/3D printed parts/Enclosure front.3mf
128.8 x 111.9 x 158.8 mm

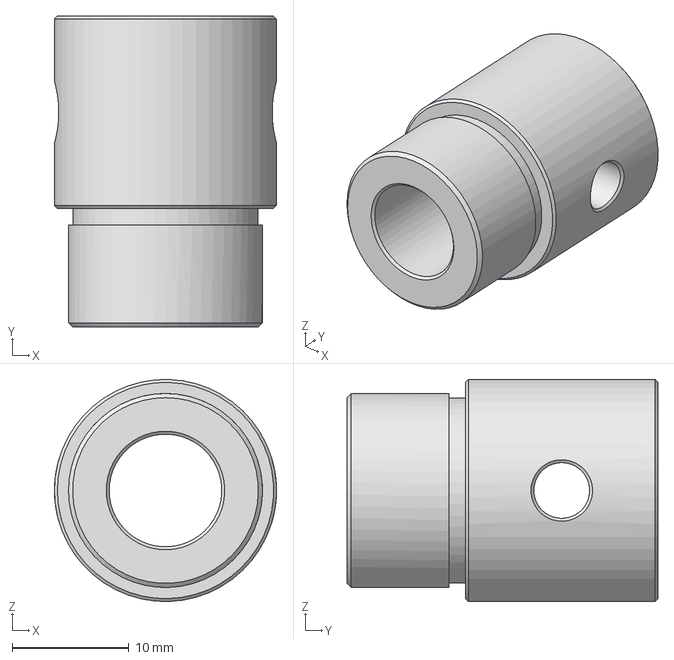
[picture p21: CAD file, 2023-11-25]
manufacturing info/Production CAD files/EV100 SS end cap v2.step
19.1 x 26.7 x 19.0 mm

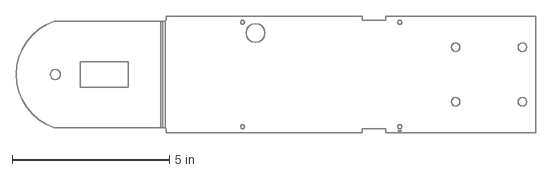
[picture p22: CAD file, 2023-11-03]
module design files/windlass/Windlass chassis V2 switch plate.dxf
16.5 x 3.72 in

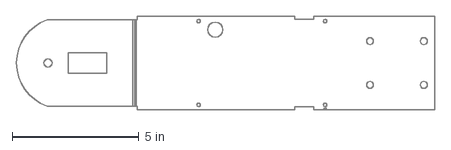
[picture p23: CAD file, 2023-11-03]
module design files/windlass/Windlass chassis V2 switch plate FINAL.dxf
16.5 x 3.72 in

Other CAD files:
manufacturing info/Production CAD files/Windlass Drum CNC design v1.step
manufacturing info/3D printed parts/Windlass cover rear.3mf
manufacturing info/3D printed parts/Enclosure rear.3mf
manufacturing info/3D printed parts/Enclosure front.stl
manufacturing info/3D printed parts/Enclosure rear.stl
manufacturing info/3D printed parts/SnP base boss.stl
manufacturing info/3D printed parts/SnP boss parts.3mf
manufacturing info/3D printed parts/Windlass Drum v1.stl
manufacturing info/3D printed parts/Windlass base mount.stl
manufacturing info/3D printed parts/Windlass cover front.3mf
manufacturing info/3D printed parts/Windlass cover rear.stl
manufacturing info/3D printed parts/Windlass drum inner.3mf
manufacturing info/3D printed parts/Windlass drum inner.stl
manufacturing info/3D printed parts/Windlass drum outer.3mf
manufacturing info/3D printed parts/Windlass hub 2.3mf
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

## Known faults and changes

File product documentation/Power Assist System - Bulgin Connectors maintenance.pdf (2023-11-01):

# Martin 16 Power-Assist System – Mk IV

Self-contained, portable, power-assisted steering and sail sheeting system

## BULGIN Connectors – care and maintenance

The Mk IV Power Assist System module
interconnect cables use a robust, water-proof connector system called the BULGIN Buccaneer. The BULGIN Buccaneer incorporates a screw-on retainer nut that assures that the connections do not come apart while sailing.

The BULGIN Buccaneer connectors are:
1) a SIX-pin male connector on each of the
a. Mk IV Joystick Module
b. Mk IV S&P Module
c. Mk IV Windlass
d. Mk IV Battery Charger
2) A SIX-pin female connector (2) on
a. Mk IV Battery Module
3) a THREE-pin male connector on
a. ST 4000+ helm drive
b. Auxiliary drive(s)
4) a THREE-pin female connector on
a. Mk IV Joystick Module –
helm drive port

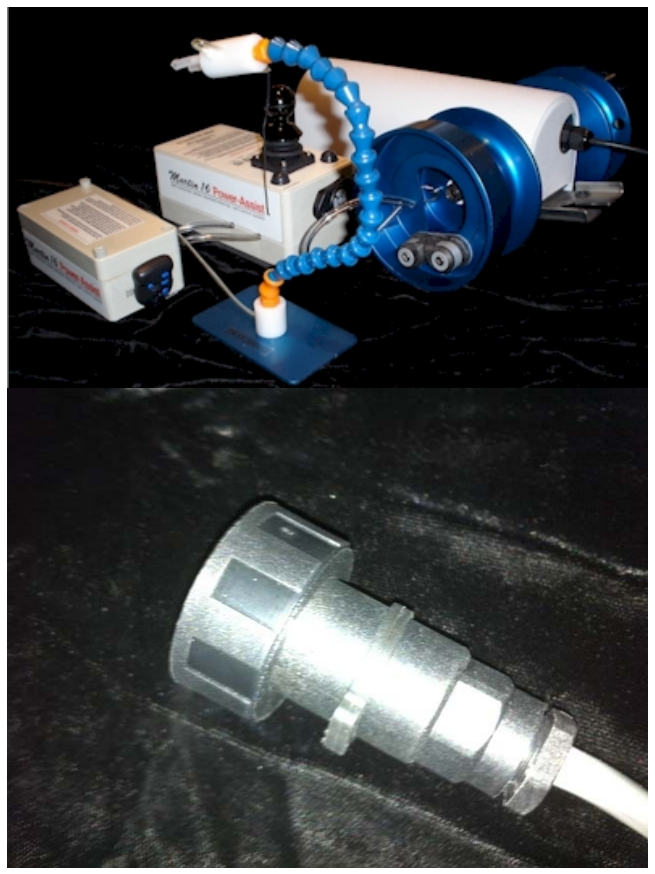
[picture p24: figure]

b. Mk IV S&P Module – helm drive port
c. Auxiliary drive port(s)

The BULGIN connectors are keyed so that they cannot be connected incorrectly; any Mk IV Module interconnect cable (male) connector may be plugged into any compatible (female) connector. The SIX-pin connector supplies 12V power (pin 1 and 2) and three CONTROL conductors (pin 4, 5, and 6) to interconnect the WINDLASS with either 1) Mk IV Joystick Module or 2) Mk IV Sip & Puff Module.

To make a connection, the male connector is inserted into the female connector. The connector is “keyed” so that the pins will engage in one orientation only. Rotate the male connector until the “keys” match, and the male and female connector faces engage so that they are “flush” with one another; when engaged correctly, there is NO GAP between the faces of the two halves of the connector.

When the connector is seated (NO GAP), the connector retainer nut may be aligned and screwed down by hand, until snug. This retainer nut must be in place to assure that the connector will not come apart while sailing.

CAUTION: the retainer nut should thread and screw on easily, it should not be forced; damage to the retainer nut threads, or female connector threads will occur.

Self-contained, portable, power-assisted steering and sail sheeting system

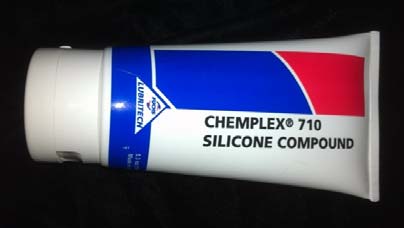
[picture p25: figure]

www.accessiblesailingtechnology.com

## BULGIN Connectors – preventative maintenance

The BULGIN Buccaneer is a robust, water-proof connector system that, with care and preventative maintenance, will provide reliable service indefinitely.

Under normal use, the male and female connector halves will mate easily, with NO GAP between the faces of the connector. In this position, the retainer nut will align and screw on easily until snug, assuring that the connector will not come apart while sailing.

Over time, with exposure to salt water and environmental contaminants, (dust, dirt, mud, etc.) the connector pins, threads, and face of the connector may become fouled and make insertion more difficult and/or foul the fine threads of the retainer nut so that it does not screw on easily.

CAUTION: if force must be used to seat the connector faces, or thread and screw on the retainer, preventative maintenance is necessary:

1) Clean and rinse both the male and
female connectors with fresh water and
a toothbrush
2) “Dress” both the male and female connector pins and faces with moisture
displacing silicon grease
(Fuchs Lubritech – Chemplex 710)
3) connect and then disconnect the “dressed” connectors several times to spread the silicon grease and establish correct connection. Make certain that the retainer nut will align and screw on without force.

As a preventative measure, inspect the Power Assist System connectors after use and, as necessary, clean and dress the connectors with silicon grease before storing the system. This routine maintenance will protect the connectors from salt water corrosion and assure that they work the next time out.

CAUTION: if you have cleaned and dressed the connectors with silicon grease, and the connector does not 1) seat easily with NO GAP between the faces, or the retainer nut does not thread and screw on easily, mechanical maintenance is necessary.
DO NOT FORCE THE CONNECTOR.

Self-contained, portable, power-assisted steering and sail sheeting system

## BULGIN Connectors – mechanical maintenance

CAUTION: if you have cleaned and dressed the connectors with silicon grease, and the connector does not 1) seat easily with NO GAP between the faces, or 2) the retainer nut does not thread and screw on easily, mechanical maintenance is necessary: DO NOT FORCE THE CONNECTOR.

The BULGIN Buccaneer is a modular connector system, assembled from interchangeable components. There are two common conditions where a Buccaneer connector may become mechanically altered so that it will not align and fit together correctly. Both of these conditions can be easily corrected as follows:

### 1. Connector “core” is loose and no longer correctly “keyed”:

With repeated use, the male or female “core” of the connector can become loose and rotate off of its “keyed” position. When this occurs, the core will become elevated and not parallel to the connector body. In this condition, the connector halves will not mate easily or completely; when you insert the male connector, you will see a gap between the faces of the connector halves. With a gap present, the retainer nut will not align and screw on easily.
This condition is most common on the female connectors on the Battery Module. It can also occur on the female helm drive connector on the Joystick or S&P Module.

When the connector “core” is no longer keyed and seated:
1) loosen the castle nut that retains the core of the connector,
2) rotate the core to re-engage the “key”,
3) re-tighten the castle nut,
4) confirm correct seating and retainer nut connection

You will require a Buccaneer “dust cap” to loosen and then re-tighten the castle nut (the dust cap has the “castle nut wrench” built in to it). There are several dust caps shipped with your system; any of these will work.

Insert the castle nut wrench (on the dust cap) over the connector core, and loosen the castle nut enough to allow the core to rotate freely. Once “keyed” the core will not rotate. So, if the core does rotate, rotate it one way and then the other until you find the “keyed” location (there is only one keyed location). When it drops into the “keyed” position, hold the core in this position and re-tighten the castle nut with your finger or
a small screw driver. Confirm that the core is still keyed
(will not rotate) and then tighten the castle nut with the

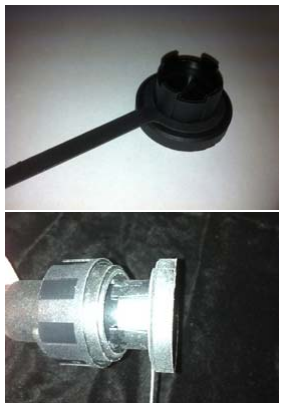
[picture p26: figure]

dust cap. When tight, view the connector from the side and confirm that the face of the core is aligned and parallel to the face of the connector body. If it is not parallel, then the core is not “keyed” and you should repeat this procedure.

CAUTION: if you cannot successfully “key” the core of the connector so that the connector halves mate properly (without a gap), replace the damaged connector(s)

Self-contained, portable, power-assisted steering and sail sheeting system

### 2. Connector “retainer band” is on the wrong side of the retainer nut:

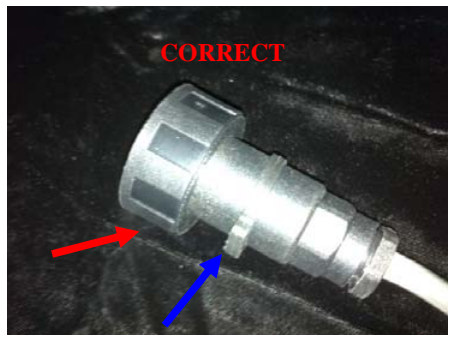
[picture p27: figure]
CORRECT

The male connectors all have a rubber
“retainer band” that keeps the retainer nut
captive on the barrel of the connector.

With repeated use, this retainer band may become loose and allow the retainer nut to come free from the connector barrel, and “float” along the power cable. The retainer band can get on the “wrong side” of the retainer nut, and jammed up against the connector barrel, preventing the retainer nut from seating properly. With the retainer band under the retainer nut, you cannot get the retainer nut thread to engage. FORCING THE RETAINER NUT WILL DAMAGE THE RETAINER NUT THREADS.

This condition is most common on the male cable connectors on 1) Mk IV Joystick Module power cable, 2) Windlass power cable, or 3)
S&P Module power cable. It can also occur on
the ST4000+ power cable connector.

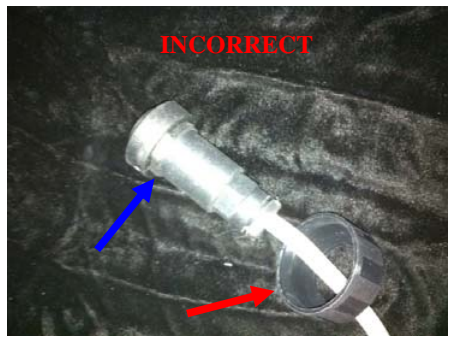
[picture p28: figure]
INCORRECT

When the retainer band is on the wrong side of the retainer nut:
1) work the retainer band off of the barrel of the connector,
2) pass the retainer band through the retainer nut,
3) slide the retainer nut back on to the barrel of the connector,
4) restore the retainer band on to the barrel of the connector, to retain the retainer nut on the barrel
5) reconnect the connector halves and confirm that the retainer nut will now align and screw on easily.

CAUTION: once you have confirmed that the retainer band is on the correct side of the retainer nut, if you cannot align and easily screw on the retainer nut, the threads of the male connector retainer nut and/or the female connector base may be permanently damaged. Replace the damaged connector(s)

Self-contained, portable, power-assisted steering and sail sheeting system

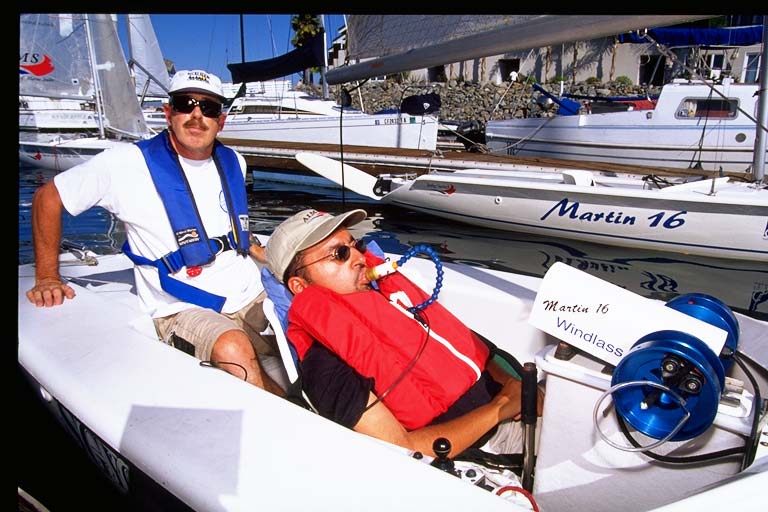
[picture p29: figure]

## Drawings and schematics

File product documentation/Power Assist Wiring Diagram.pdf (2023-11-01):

# Martin 16 Power-Assist System – Mk IV

Self-contained, portable, power-assisted steering and sail sheeting system

## “House power” wiring Harness

Any 12V power source can
provide power to Mk IV Power
Assist System Module, ,
including: 1) the portable Power-Assist Mk IV Battery Module or 2) “house power” on boats equipped with 12V DC power.

Power is supplied through
TWO six-pin female BULGIN
connectors. Any Mk IV Module
may be plugged into either
connector.

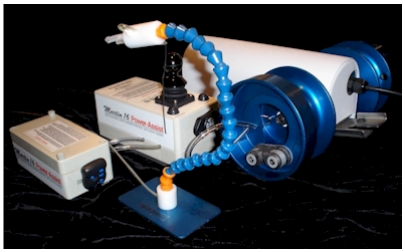
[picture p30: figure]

In addition to supplying 12V power (pin 1 and 2), the wiring harness includes three CONTROL conductors (pin 4, 5, and 6) to interconnect the WINDLASS with either 1) Mk IV Joystick Module or 2) Mk IV Sip & Puff Module.

The wiring of the two connectors is as follows:

Pin # | Function | Wire color (typical)
1 | +12V | RED (CAN) or BROWN (UK)
2 | GND | BLACK(CAN) or BLUE (UK)
3 | N/C | N/C
4 | WINDLASS LAMP | YELLOW
5 | WINDLASS “OUT” | GREEN
6 | WINDLASS “IN” | WHITE

CAUTION: The +12V power lead from the house battery must include an in-line 30A fuse (circuit breaker) in the wiring harness.

CAUTION: The pin numbers on the BULGIN connectors are imprinted into the plastic, located on the BACK FACE of the connector, near each pin fastener. These pin designations are very small and will require a magnifying glass to read.

# Power-Assist System – Mk IV

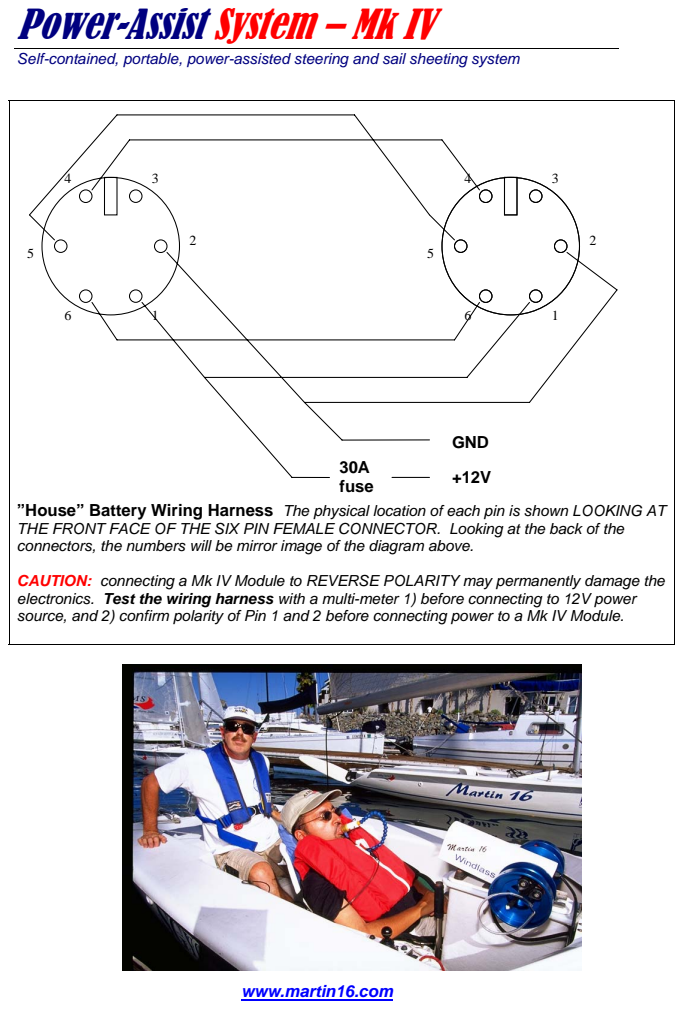
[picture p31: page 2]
www.martin16.com; GND; 30A fuse

Self-contained, portable, power-assisted steering and sail sheeting system

”House” Battery Wiring Harness The physical location of each pin is shown LOOKING AT
THE FRONT FACE OF THE SIX PIN FEMALE CONNECTOR. Looking at the back of the
connectors, the numbers will be mirror image of the diagram above.

CAUTION: connecting a Mk IV Module to REVERSE POLARITY may permanently damage the
electronics. Test the wiring harness with a multi-meter 1) before connecting to 12V power
source, and 2) confirm polarity of Pin 1 and 2 before connecting power to a Mk IV Module.

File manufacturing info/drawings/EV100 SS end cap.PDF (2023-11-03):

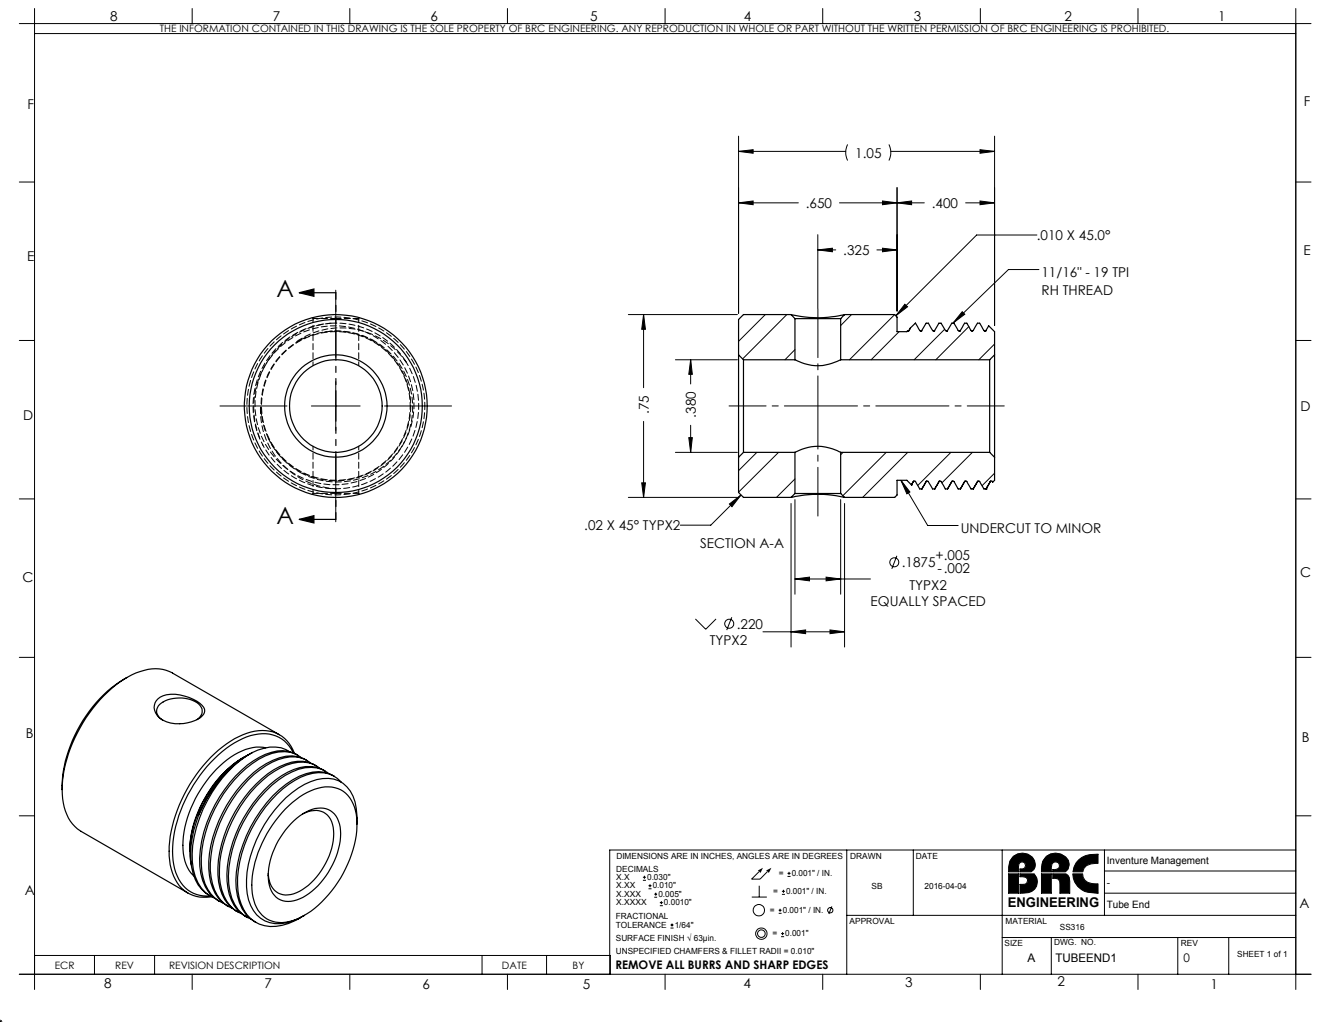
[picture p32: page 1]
.02 X 45° TYPX2; EQUALLY SPACED; SECTION A-A; UNDERCUT TO MINOR; 11/16" - 19 TPI RH THREAD; ECR; REV; REVISION DESCRIPTION; DATE; SIZE; DWG. NO.; SHEET 1 of 1; Tube End; Inventure Management; REMOVE ALL BURRS AND SHARP EDGES

THE INFORMATION CONTAINED IN THIS DRAWING IS THE SOLE PROPERTY OF BRC ENGINEERING. ANY REPRODUCTION IN WHOLE OR PART WITHOUT THE WRITTEN PERMISSION OF BRC ENGINEERING IS PROHIBITED.

DIMENSIONS ARE IN INCHES, ANGLES ARE IN DEGREES
DECIMALS
FRACTIONAL
TOLERANCE 1/64"
SURFACE FINISH √ 63µin.
UNSPECIFIED CHAMFERS & FILLET RADII = 0.010"

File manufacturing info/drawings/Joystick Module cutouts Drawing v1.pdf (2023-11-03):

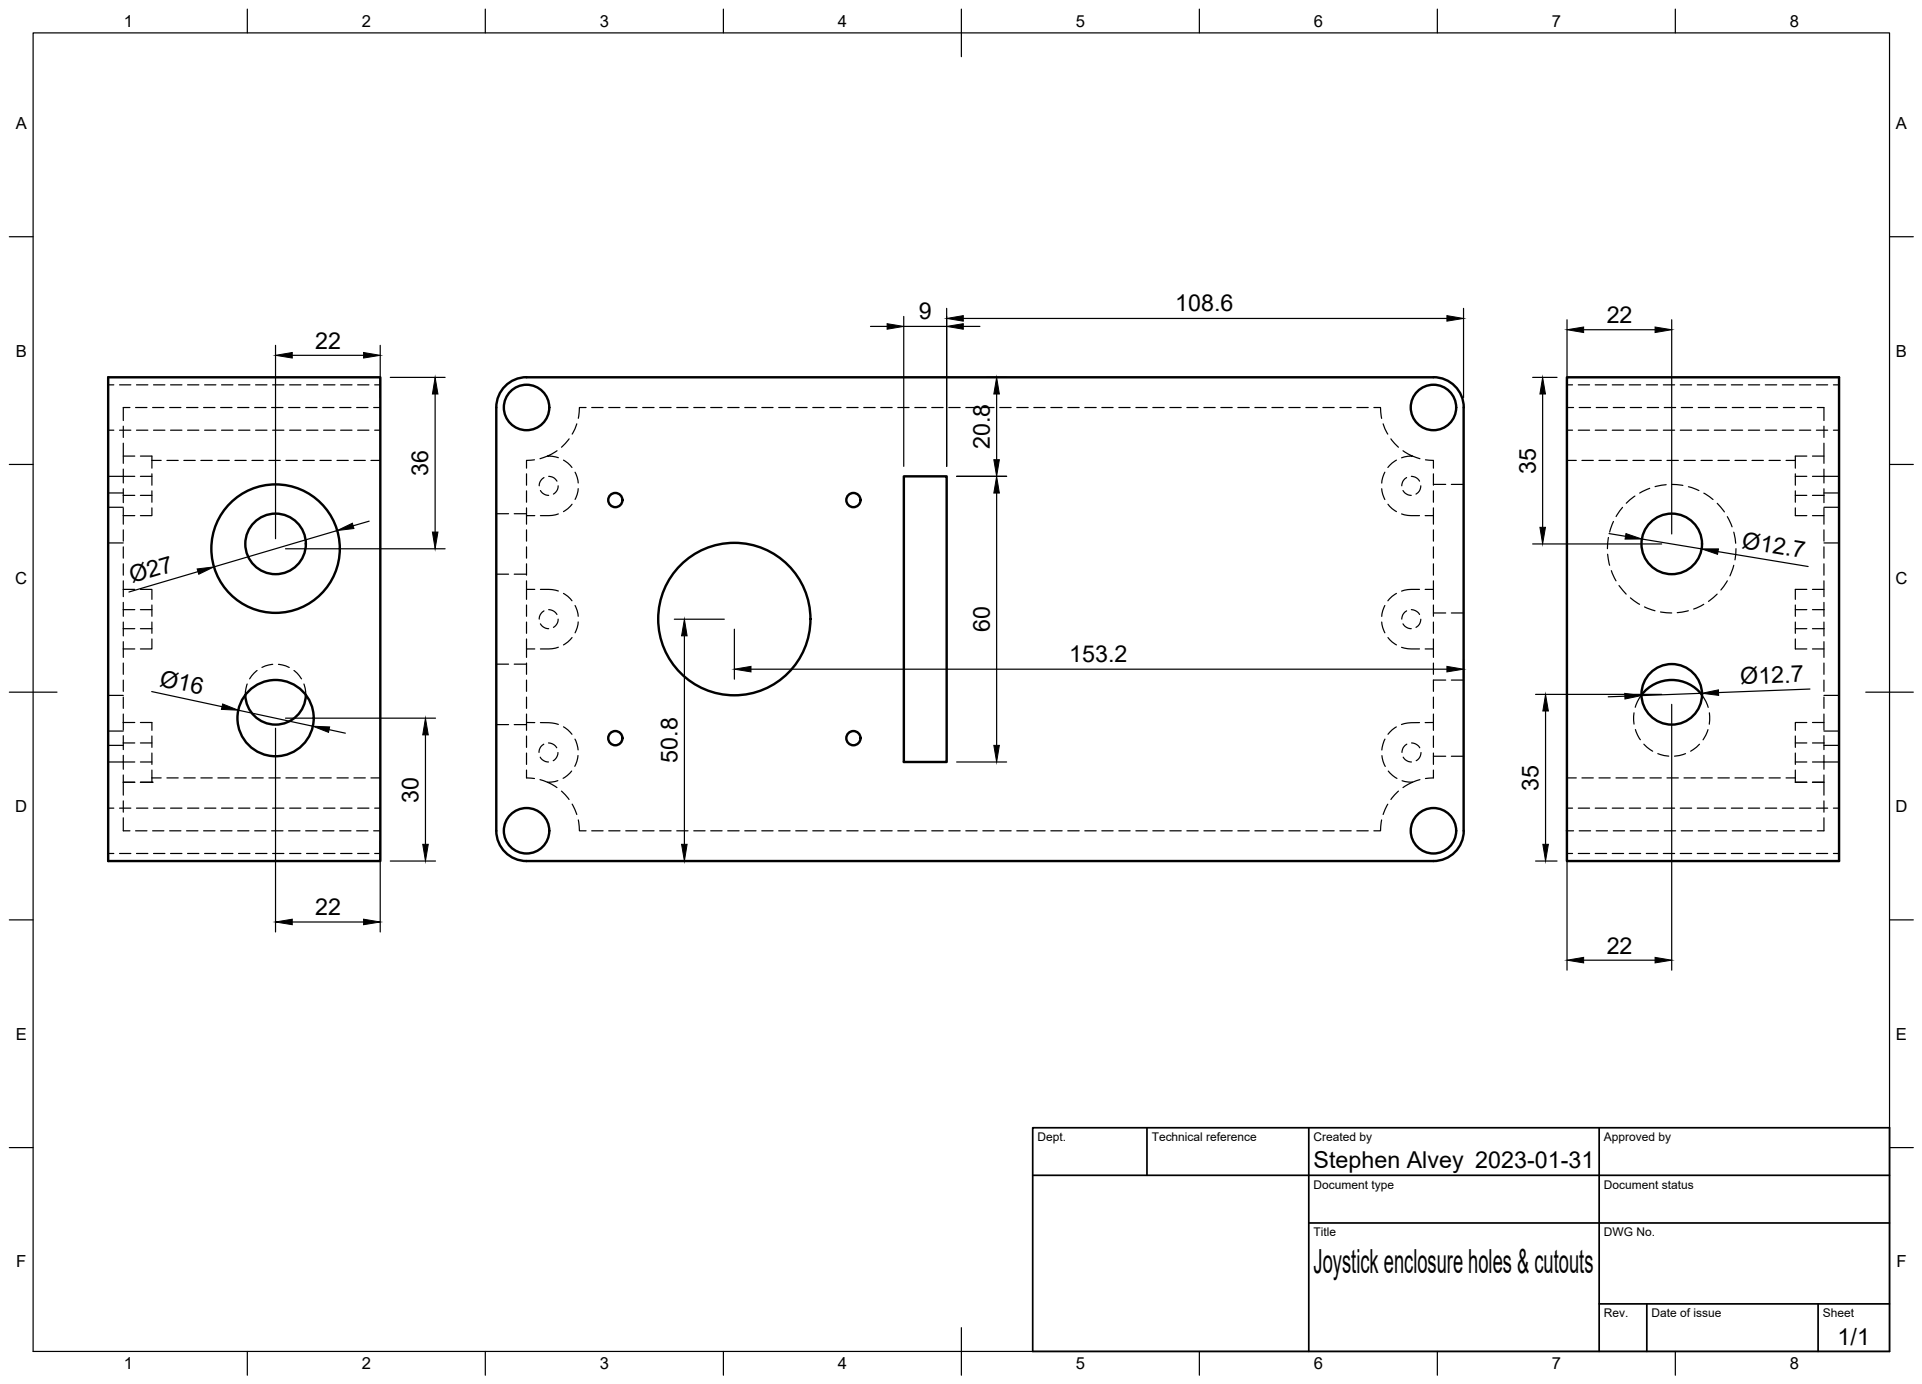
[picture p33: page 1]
Title; DWG No.; Rev.; Date of issue; Sheet; Stephen Alvey 30 36

Dept. | Technical reference | Created by 2023-01-31 | Approved by

Document type | Document status

Joystick enclosure holes & cutouts

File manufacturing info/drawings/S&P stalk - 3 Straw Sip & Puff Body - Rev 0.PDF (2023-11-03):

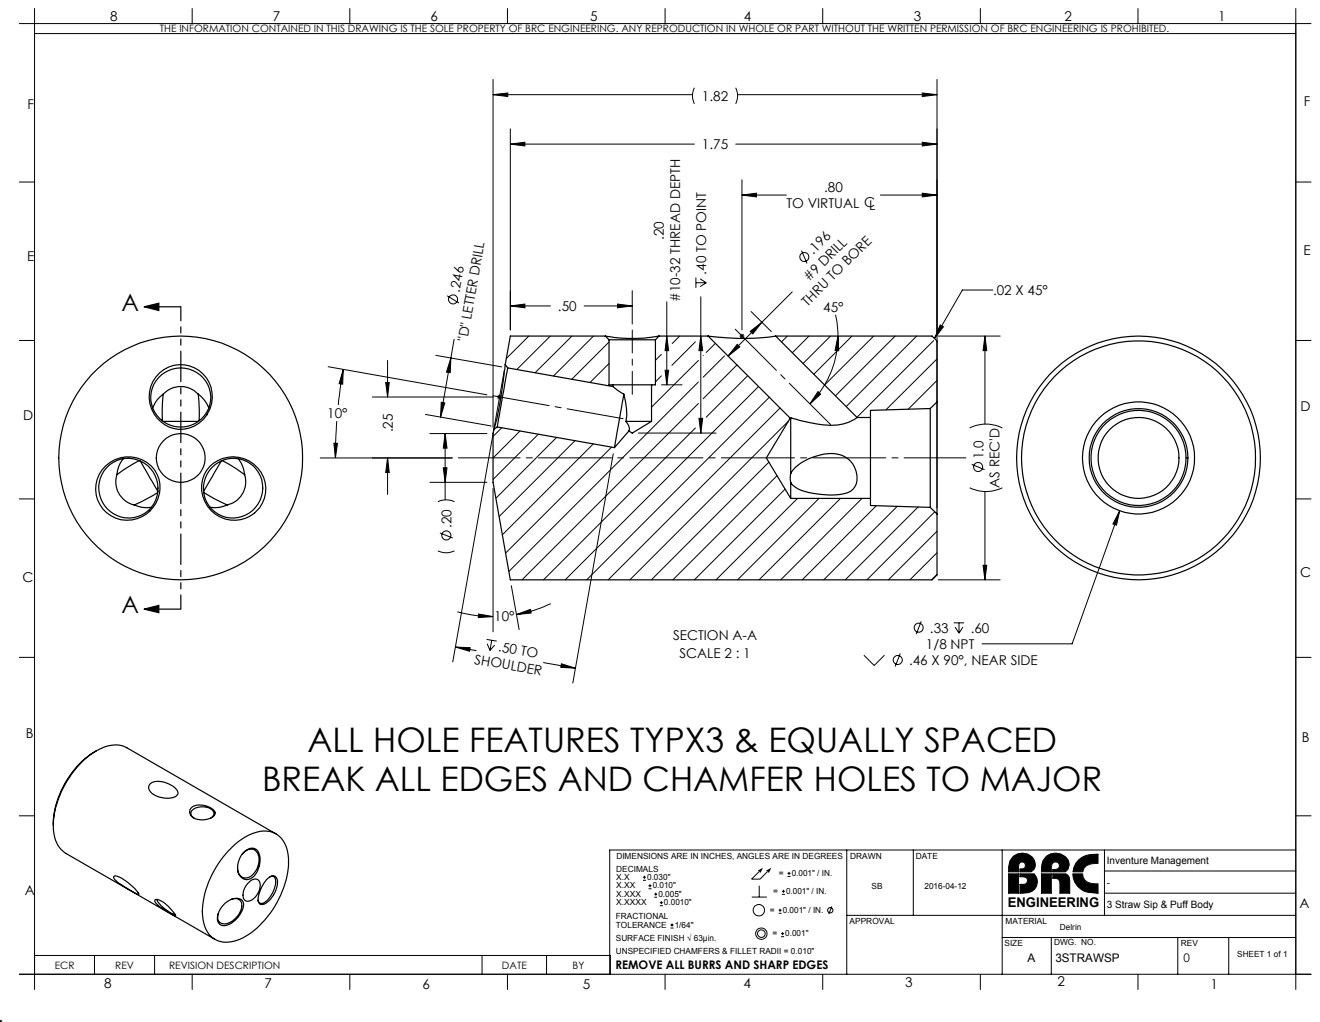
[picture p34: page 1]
"D" LETTER DRILL; #10-32 THREAD DEPTH; .40 TO POINT; #9 DRILL; AS REC'D; SECTION A-A SCALE 2 : 1; .33 .60 1/8 NPT .46 X 90°, NEAR SIDE; ECR; REV; REVISION DESCRIPTION; DATE; SIZE; DWG. NO.; SHEET 1 of 1; REMOVE ALL BURRS AND SHARP EDGES

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

TO VIRTUAL CL

THRU TO BORE

ALL HOLE FEATURES TYPX3 & EQUALLY SPACED
BREAK ALL EDGES AND CHAMFER HOLES TO MAJOR

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

Inventure Management
3 Straw Sip & Puff Body

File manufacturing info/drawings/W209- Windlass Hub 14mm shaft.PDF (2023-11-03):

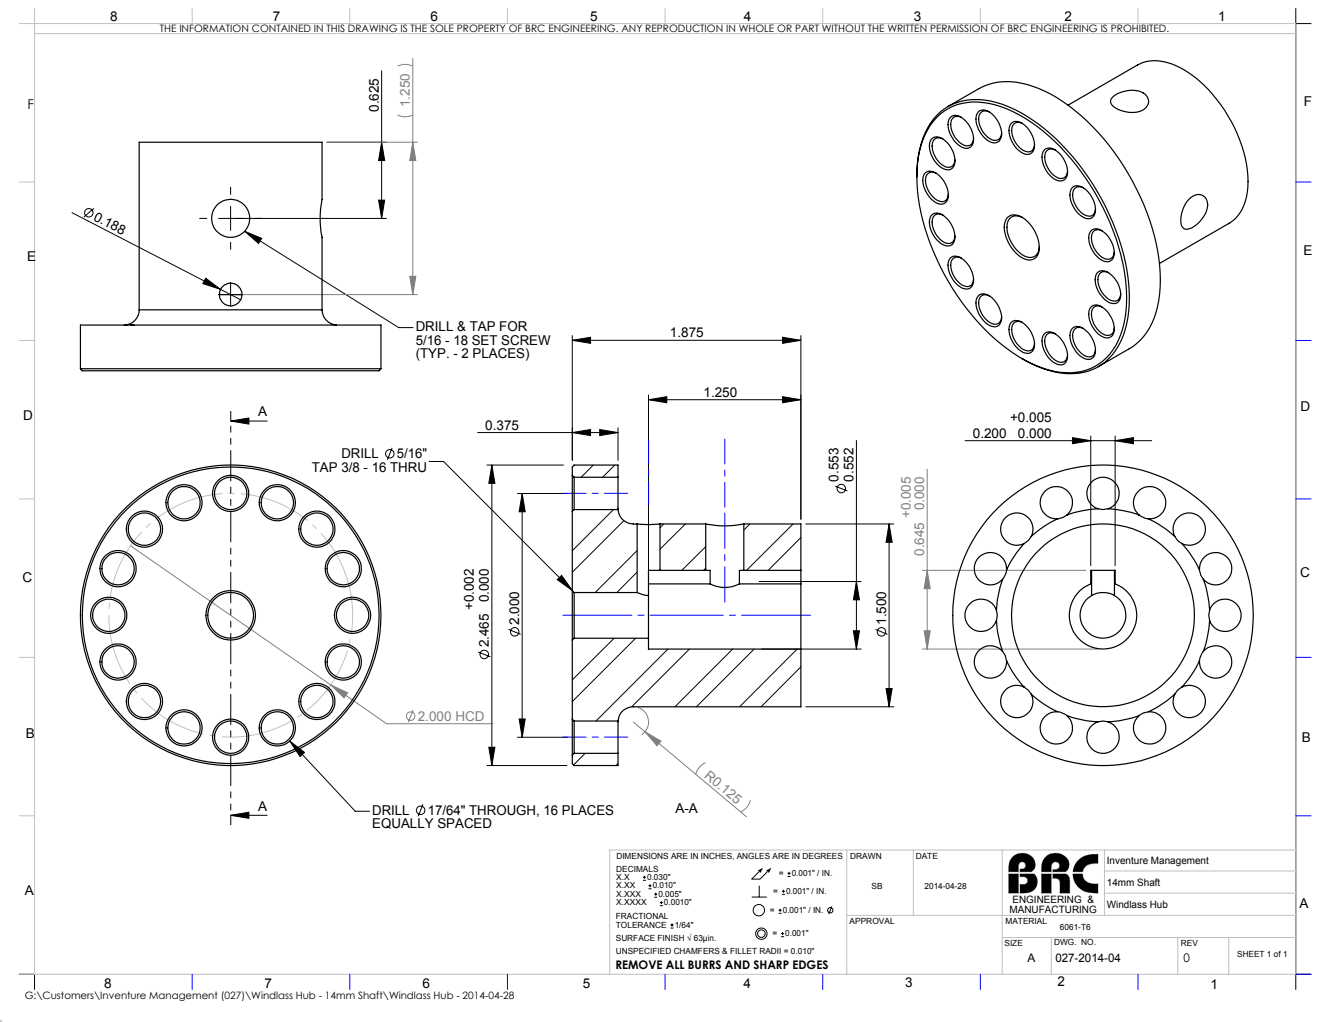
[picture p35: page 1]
2.000 HCD; DRILL 17/64" THROUGH, 16 PLACES; EQUALLY SPACED; DRILL 5/16" TAP 3/8 - 16 THRU; SIZE; DWG. NO.; SHEET 1 of 1; Windlass Hub; Inventure Management; 14mm Shaft; REMOVE ALL BURRS AND SHARP EDGES; ENGINEERING &

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

DRILL & TAP FOR
5/16 - 18 SET SCREW
(TYP. - 2 PLACES)

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

G:\Customers\Inventure Management (027)\Windlass Hub - 14mm Shaft\Windlass Hub - 2014-04-28

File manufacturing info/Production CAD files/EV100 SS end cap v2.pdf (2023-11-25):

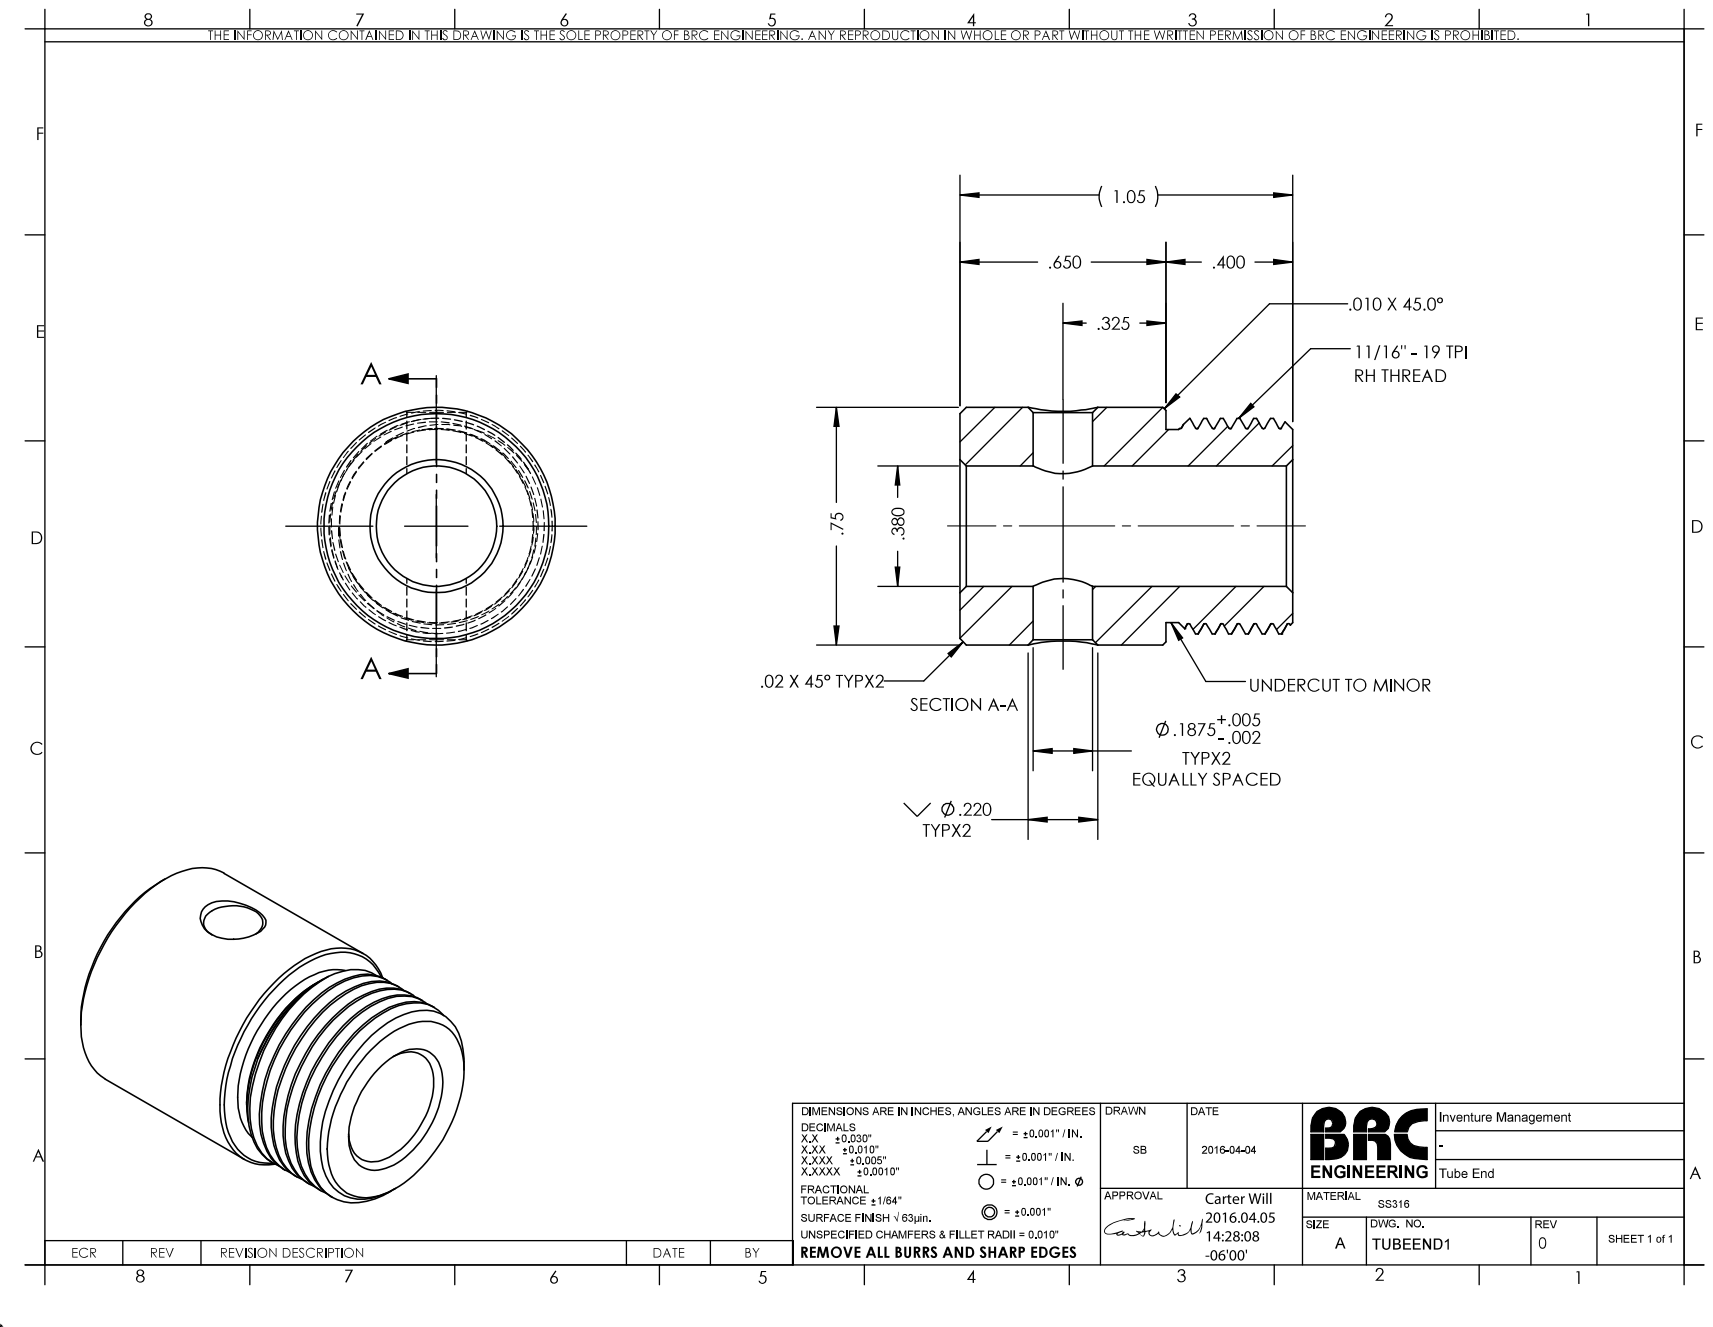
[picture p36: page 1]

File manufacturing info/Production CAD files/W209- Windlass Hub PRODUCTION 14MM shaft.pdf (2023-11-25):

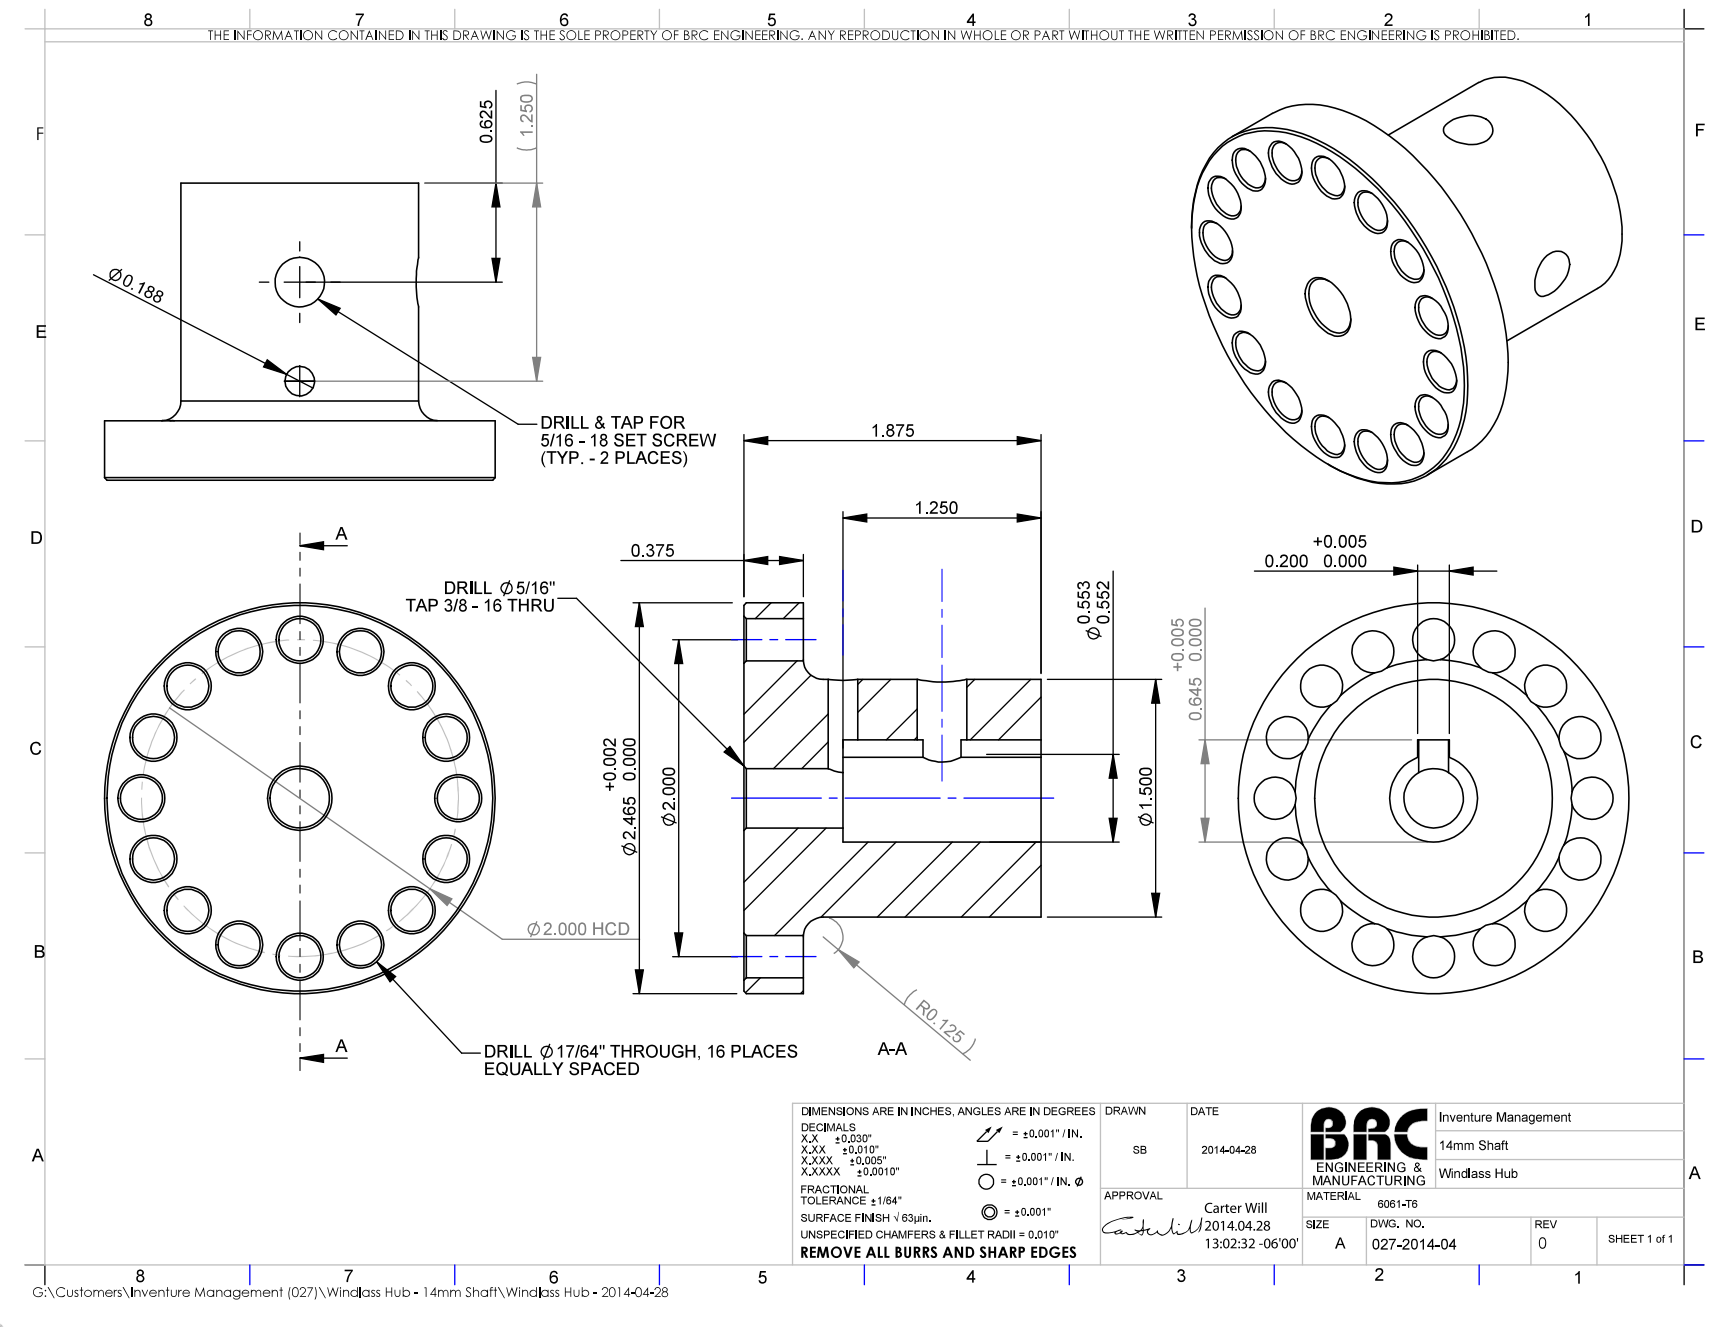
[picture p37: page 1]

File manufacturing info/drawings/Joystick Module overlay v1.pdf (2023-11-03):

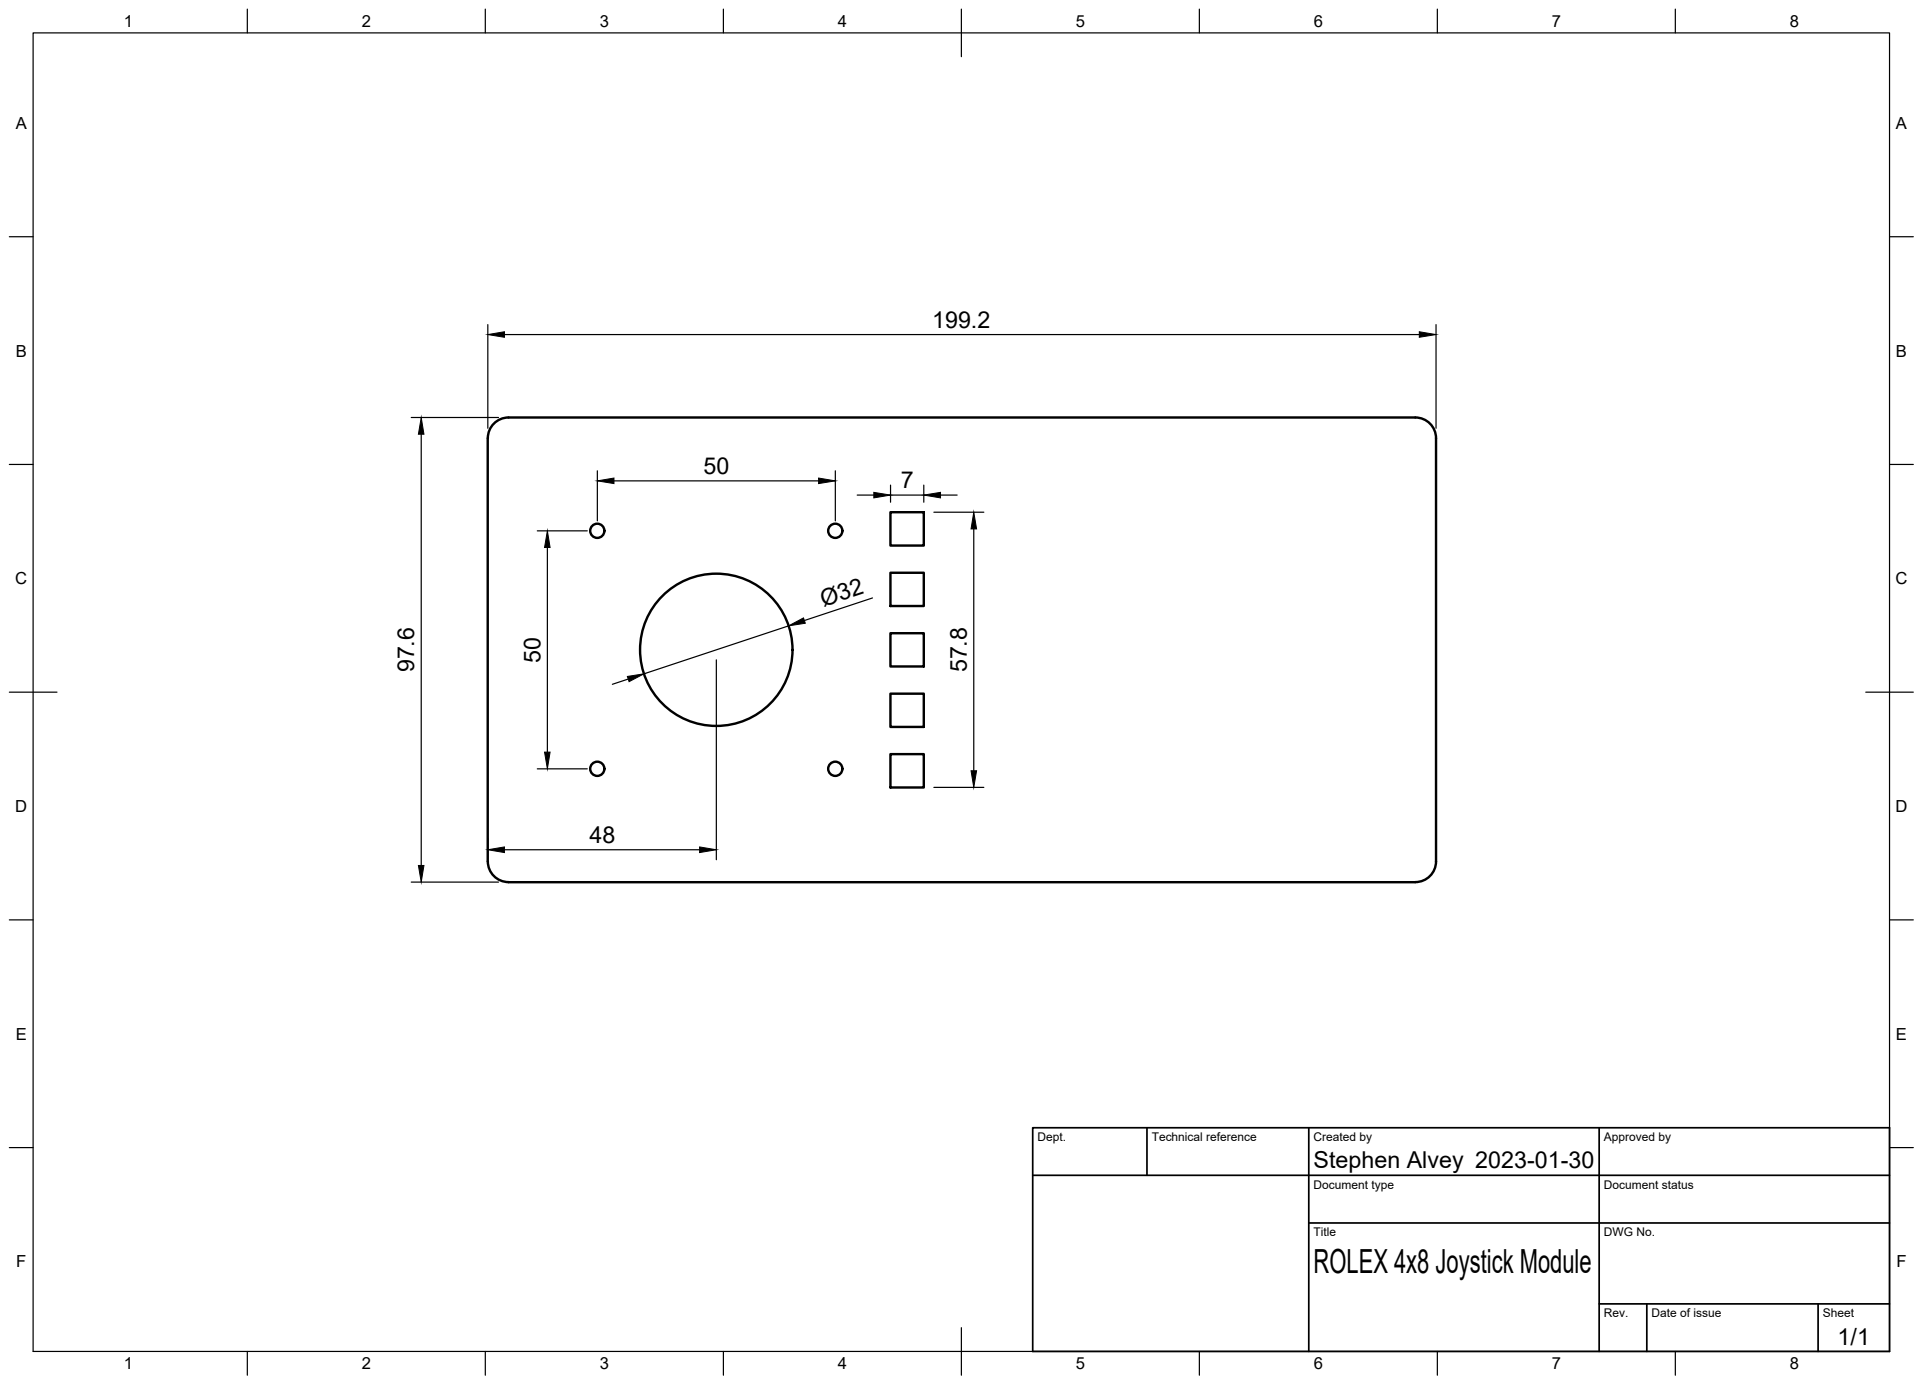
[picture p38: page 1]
Title; DWG No.; Rev.; Date of issue; Sheet

Dept. | Technical reference | Created by Stephen Alvey 2023-01-30 | Approved by

Document type | Document status

ROLEX 4x8 Joystick Module

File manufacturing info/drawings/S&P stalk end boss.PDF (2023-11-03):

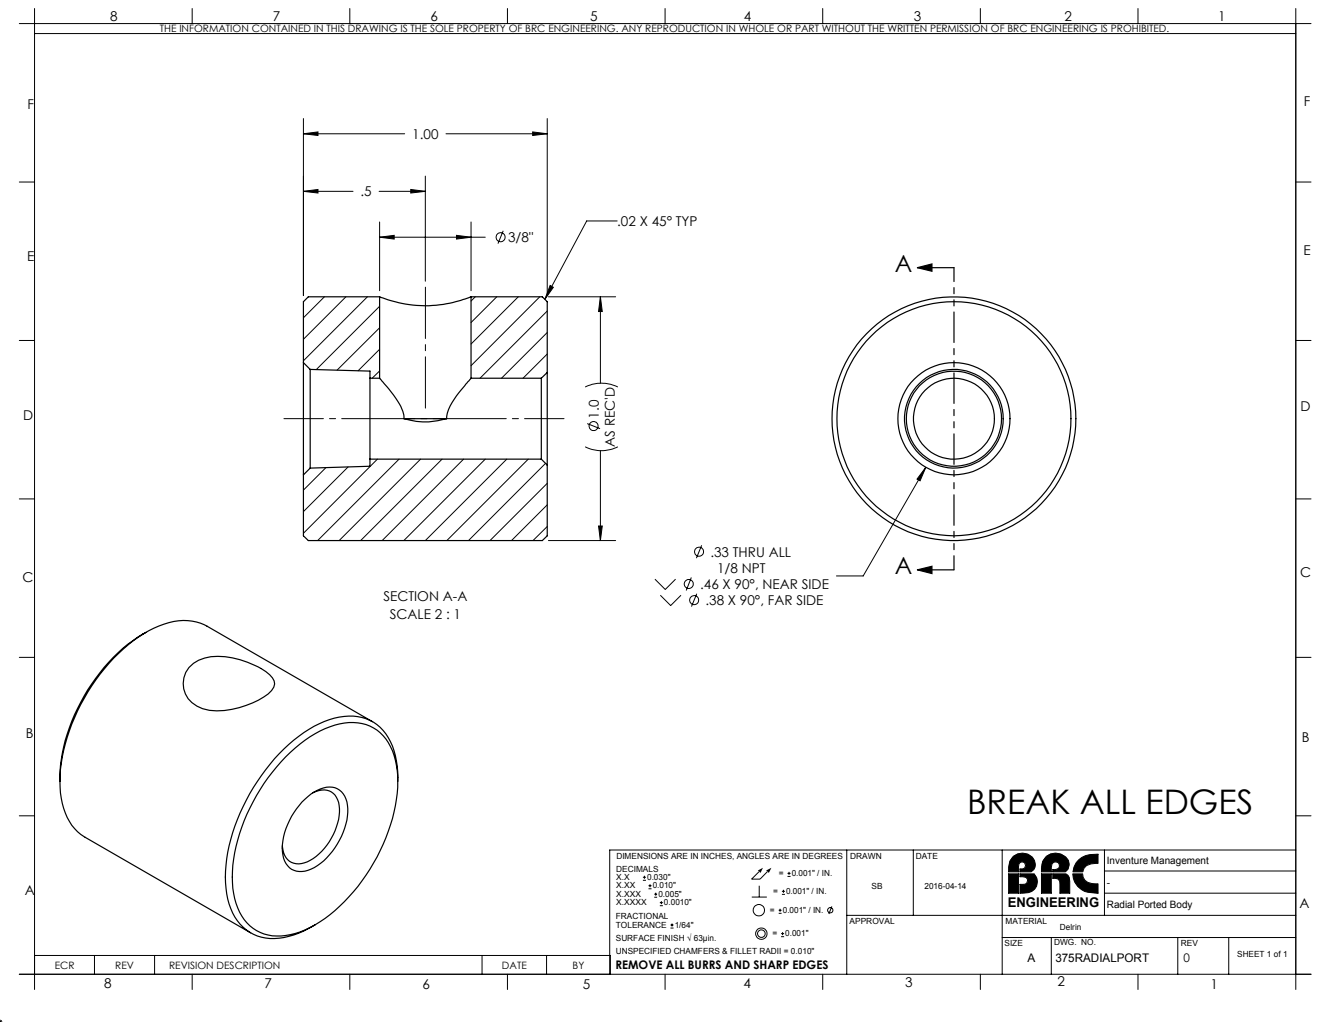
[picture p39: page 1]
.33 THRU ALL 1/8 NPT .46 X 90°, NEAR SIDE .38 X 90°, FAR SIDE; AS REC'D; .02 X 45° TYP; SECTION A-A SCALE 2 : 1; ECR; REV; REVISION DESCRIPTION; DATE; SIZE; DWG. NO.; SHEET 1 of 1; REMOVE ALL BURRS AND SHARP EDGES

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

BREAK ALL EDGES

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

Inventure Management
Radial Ported Body

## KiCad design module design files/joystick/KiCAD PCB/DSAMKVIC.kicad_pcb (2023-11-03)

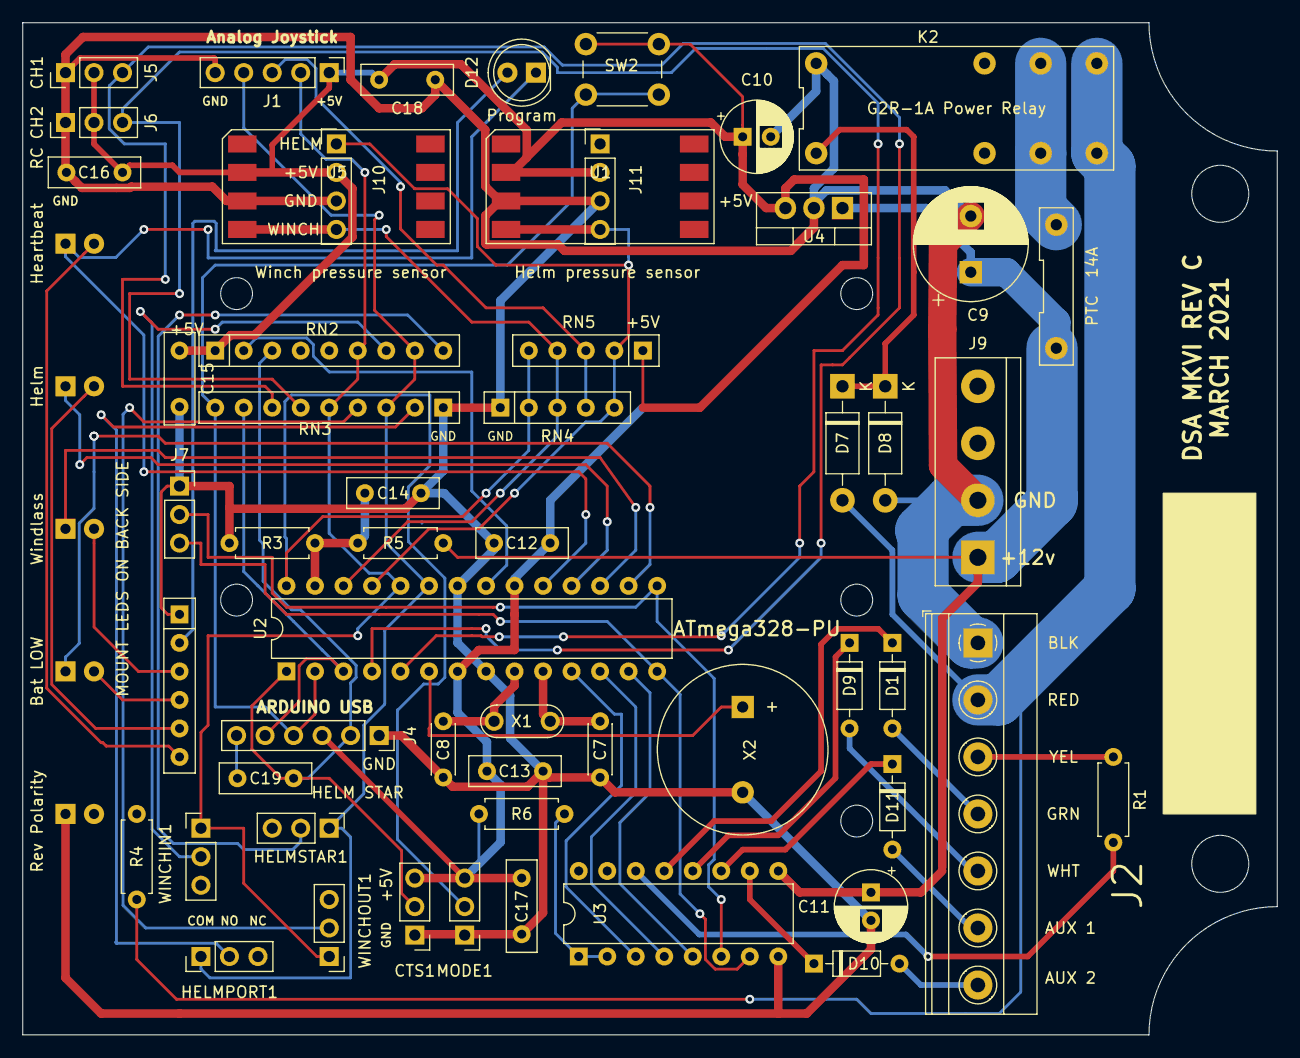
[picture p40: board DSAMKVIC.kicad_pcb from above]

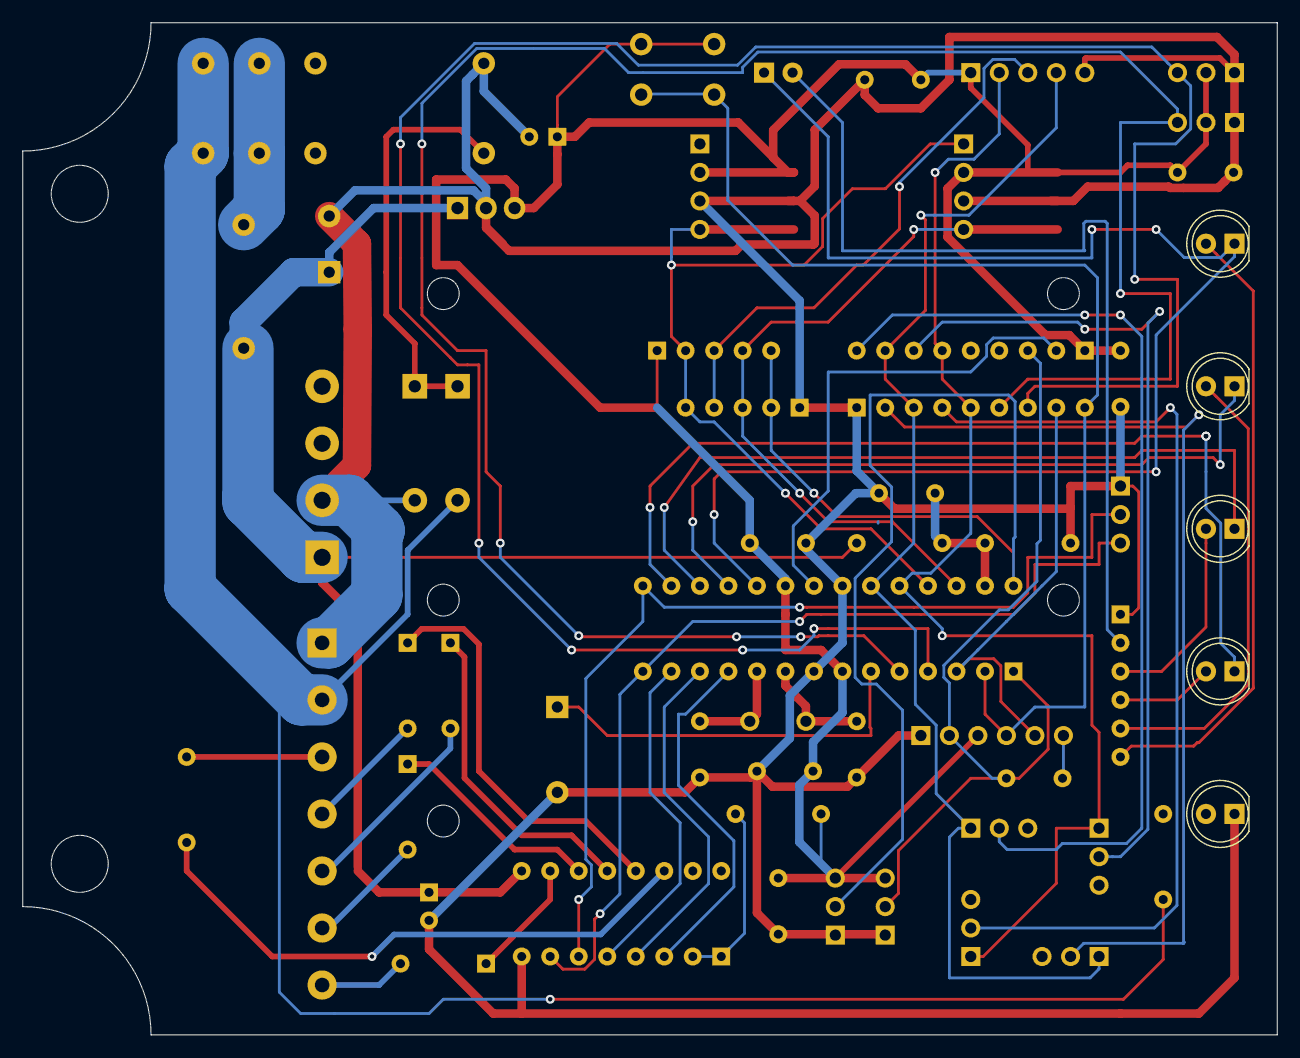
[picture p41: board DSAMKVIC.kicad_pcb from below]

Board: 2 copper layers, 111.8 x 90.2 mm, 60 parts (5 on the bottom side), 53 nets.

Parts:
C7, C8: 22 pF; C_Disc_D4.3mm_W1.9mm_P5.00mm
C9: 1000 uF 16V; CP_Radial_D10.0mm_P5.00mm
C10: 10 uF 16V; CP_Radial_D6.3mm_P2.50mm
C11: 10uF 16V; CP_Radial_D6.3mm_P2.50mm
C12, C13, C15, C16, C17, C18: .47uF 50V; C_Disc_D8.0mm_W2.5mm_P5.00mm
C14: 4N7; C_Disc_D8.0mm_W2.5mm_P5.00mm
C19: .1uF 50V; C_Disc_D8.0mm_W2.5mm_P5.00mm
CTS1: Jumper_CTS; PinHeader_1x03_P2.54mm_Vertical
D1, D9, D10, D11: BAT48RL; D_DO-35_SOD27_P7.62mm_Horizontal
D2: Heartbeat; LED_D5.0mm
D3: Helm; LED_D5.0mm
D4: Windlass; LED_D5.0mm
D5: Bat LOW; LED_D5.0mm
D6: Rev Polarity; LED_D5.0mm
D7, D8: 1N4001; D_DO-41_SOD81_P10.16mm_Horizontal
D12: Program LED; LED_D5.0mm
F1: PTC 14A; PTC14
HELMPORT1: HELM PORT; PinHeader_1x03_P2.54mm_Vertical
HELMSTAR1: HELM STAR; PinHeader_1x03_P2.54mm_Vertical
J1: Analog Joystick; PinHeader_1x05_P2.54mm_Vertical
J2: .200 EURO; TerminalBlock_Phoenix_MKDS-1,5-7-5.08_1x07_P5.08mm_Horizont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
J4: USB; PinSocket_1x06_P2.54mm_Vertical
J5: CH1; PinHeader_1x03_P2.54mm_Vertical
J6: CH2; PinHeader_1x03_P2.54mm_Vertical
J7: Cytron PWM; PinSocket_1x03_P2.54mm_Vertical
J9: Cytron Pwr; TerminalBlock_bornier-4_P5.08mm
J10: S&P WINCH; PinHeader_1x04_P2.54mm_Vertical
J11: S&P HELM; PinHeader_1x04_P2.54mm_Vertical
K2: G2R-1A Power Relay; G2R-1A
MODE1: Jumper_MODE; PinHeader_1x03_P2.54mm_Vertical
R1: 470R; R_Axial_DIN0207_L6.3mm_D2.5mm_P7.62mm_Horizontal
R3: 4.9K; R_Axial_DIN0207_L6.3mm_D2.5mm_P7.62mm_Horizontal
R4: 1K; R_Axial_DIN0207_L6.3mm_D2.5mm_P7.62mm_Horizontal
R5: 11K; R_Axial_DIN0207_L6.3mm_D2.5mm_P7.62mm_Horizontal
R6: 10K; R_Axial_DIN0207_L6.3mm_D2.5mm_P7.62mm_Horizontal
RN1: 470R; R_Array_SIP6
RN2, RN3: 10K; R_Array_SIP9
RN4, RN5: 100K SIP; R_Array_SIP5
SW2: Program; SW_PUSH_6mm_H4.3mm
U1: Helm pressure sensor; MPXV7007
U2: ATmega328-PU; DIP-28_W7.62mm
U3: ULN2003; DIP-16_W7.62mm
U4: L7805; TO-220-3_Vertical
U5: Winch pressure sensor; MPXV7007
WINCHIN1: WINCH IN; PinHeader_1x03_P2.54mm_Vertical
WINCHOUT1: WINCH OUT; PinHeader_1x03_P2.54mm_Vertical
X1: 16 mhz xtal; Resonator-2Pin_W7.0mm_H2.5mm
X2: Buzzer; Buzzer_15x7.5RM7.6

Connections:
+5V: C10.1, C12.1, C13.1, C15.1, C16.1, C17.1, C18.1, CTS1.3, J1.1, J4.3, J5.2, J6.2, J10.2, J11.2, MODE1.3, R6.1, RN2.1, RN5.1, SW2.1, U1.2, U2.7, U2.20, U4.3, U5.2
+12V: C9.1, C11.1, F1.1, J9.1, R5.1, U3.9, U4.1
+BATT: D7.2, J2.2, K2.4, K2.5, R4.1
CH1: J5.3, RN3.7, U2.4
CH2: J6.3, RN3.6, U2.5
GNDREF: C7.2, C8.2, C9.2, C10.2, C11.2, C12.2, C13.2, C14.2, C15.2, C16.2, C17.2, C18.2, CTS1.1, D6.1, D8.2, J1.5, J2.1, J4.1, J5.1, J6.1, J7.1, J9.2, J10.3, J11.3, K2.8, MODE1.1, R3.2, RN1.1, RN3.1, RN4.1, U1.3, U2.8, U2.22, U3.8, U4.2, U5.3, X2.2
unnamed: C7.1, U2.10, X1.1
unnamed: C8.1, U2.9, X1.2
unnamed: C14.1, R3.1, R5.2, U2.27
unnamed: C19.1, CTS1.2, J4.2, RN2.3, U2.1
unnamed: C19.2, J4.6
unnamed: D1.1, U3.13
unnamed: D1.2, J2.4
unnamed: D2.2, RN1.6
unnamed: D3.1, U2.18
unnamed: D3.2, RN1.5
unnamed: D4.1, U2.17
unnamed: D4.2, RN1.3
unnamed: D5.1, U2.16
unnamed: D5.2, RN1.4
unnamed: D6.2, R4.2
unnamed: D7.1, D8.1, K2.1
unnamed: D9.1, U3.12
unnamed: D9.2, J2.5
unnamed: D10.1, U3.10
unnamed: D10.2, J2.7
unnamed: D11.1, U3.11
unnamed: D11.2, J2.6
unnamed: D2.1, D12.1, U2.19
unnamed: D12.2, RN1.2
unnamed: F1.2, K2.3, K2.6
unnamed: HELMPORT1.1, HELMSTAR1.1, J1.4, RN2.8, RN3.3, U2.23
unnamed: HELMPORT1.2, RN3.2
unnamed: HELMSTAR1.2, RN2.9
unnamed: J1.2, RN2.6, RN3.5, U2.24, WINCHIN1.1, WINCHOUT1.1
unnamed: J1.3, RN4.4, RN5.3
unnamed: J2.3, R1.1
unnamed: J4.4, RN3.9, SW2.2, U2.2
unnamed: J4.5, RN3.8, U2.3
unnamed: J7.2, U2.15, U3.6
unnamed: J7.3, U2.14, U3.7
unnamed: J10.1, J11.4, RN4.5, RN5.2, U1.4, U2.25
unnamed: J10.4, RN4.3, RN5.4, U2.26, U5.4
unnamed: MODE1.2, RN4.2, RN5.5, U2.28
unnamed: R1.2, U3.14
unnamed: R6.2, U3.1, U3.2
unnamed: RN2.2, U2.21
unnamed: RN2.7, WINCHIN1.2
unnamed: RN3.4, WINCHOUT1.2
unnamed: U2.6, X2.1
unnamed: U2.11, U3.3
unnamed: U2.12, U3.4
unnamed: U2.13, U3.5

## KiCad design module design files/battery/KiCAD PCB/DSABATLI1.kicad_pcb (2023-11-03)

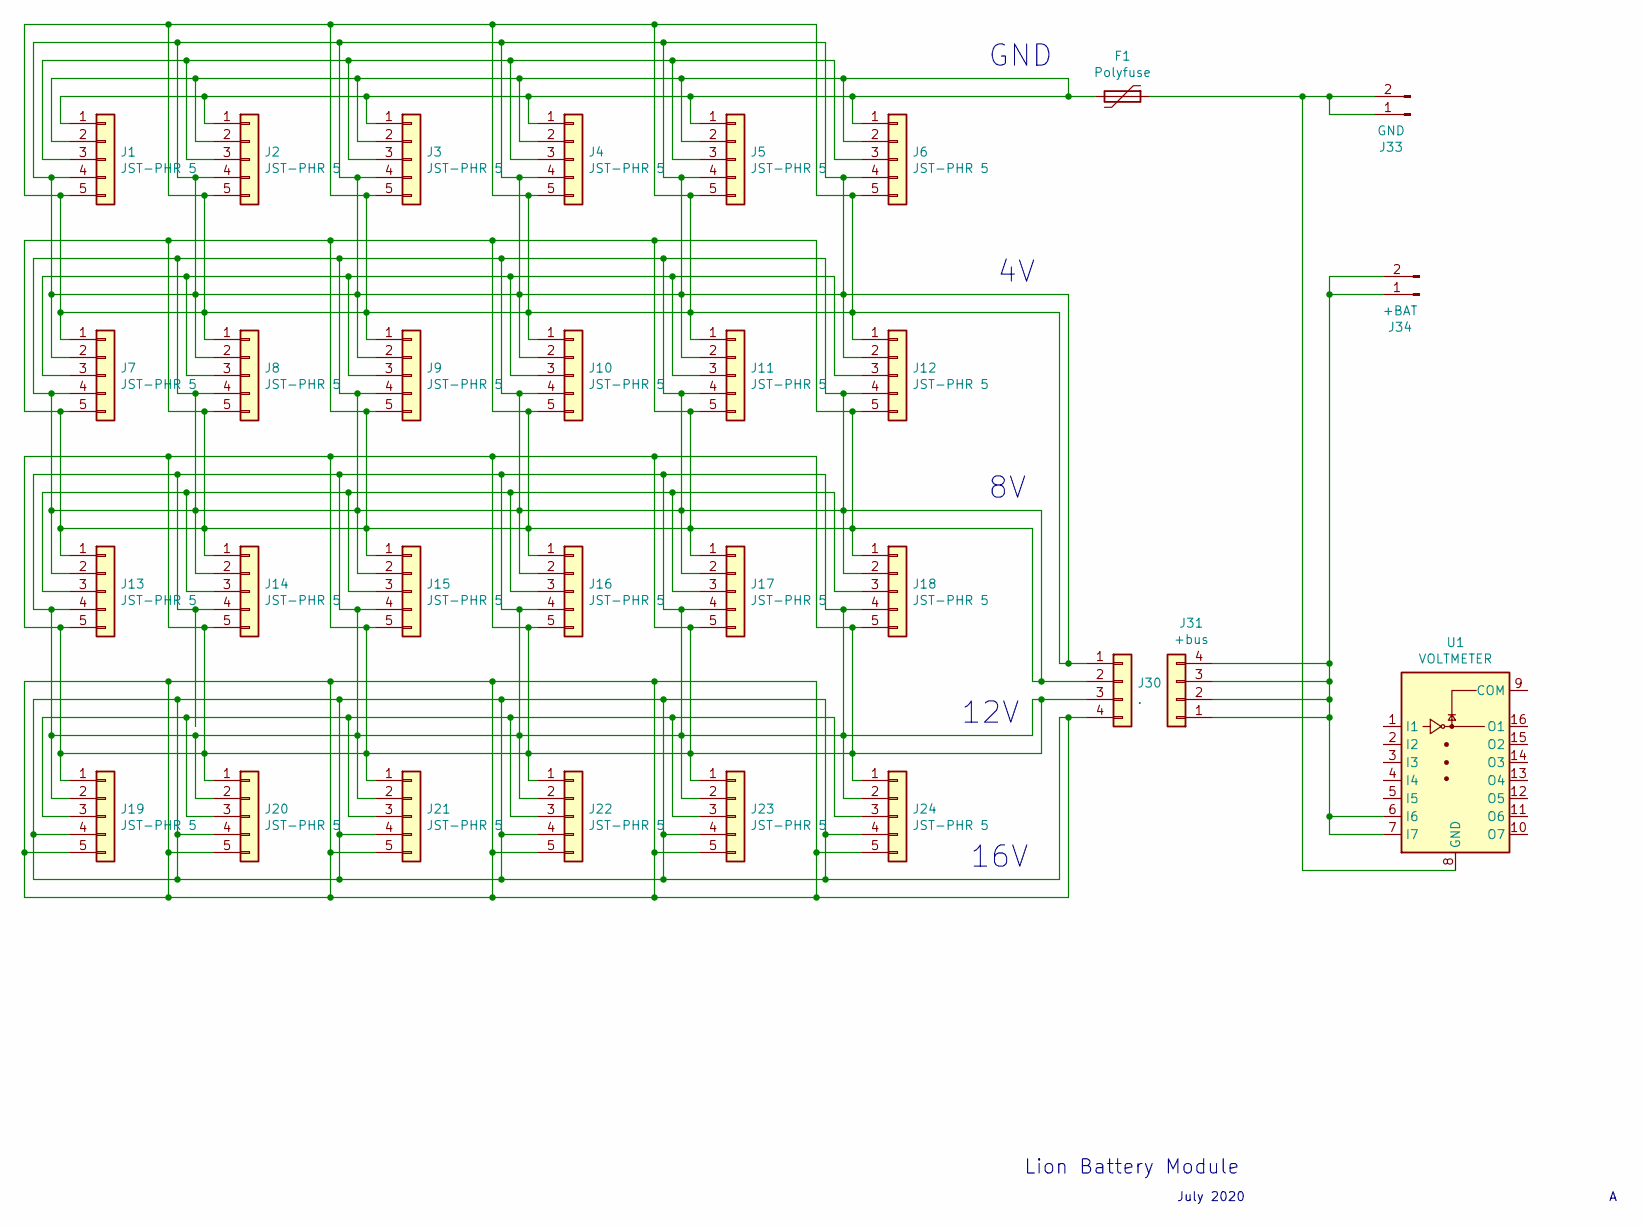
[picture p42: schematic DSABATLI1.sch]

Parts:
F1: Polyfuse; Fuse_Bourns_MF-RHT1000
J1, J2, J3, J4, J5, J6, J7, J8, J9, J10, J11, J12, J13, J14, J15, J16, J17, J18, J19, J20, J21, J22, J23, J24: JST-PHR 5; JST_PH_B5B-PH-K_1x05_P2.00mm_Vertical
J30: .; SolderWirePad_1x04_P5.08mm_Drill1.5mm
J31: +bus; SolderWirePad_1x04_P5.08mm_Drill1.5mm
J33: GND; SolderWirePad_1x02_P7.62mm_Drill2.5mm
J34: +BAT; SolderWirePad_1x02_P7.62mm_Drill2.5mm
U1: VOLTMETER; DIP-16_W10.16mm

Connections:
unnamed 0: F1.1, J33.1, J33.2, U1.8 (GND); also elsewhere on the board
unnamed 1: F1.2, J1.1, J1.2, J2.1, J2.2, J3.1, J3.2, J4.1, J4.2, J5.1, J5.2, J6.1, J6.2; also elsewhere on the board
unnamed: J1.3, J2.3, J3.3, J4.3, J5.3, J6.3
unnamed: J1.4, J1.5, J2.4, J2.5, J3.4, J3.5, J4.4, J4.5, J5.4, J5.5, J6.4, J6.5, J7.1, J7.2, J8.1, J8.2, J9.1, J9.2, J10.1, J10.2, J11.1, J11.2, J12.1, J12.2, J30.1
unnamed: J7.3, J8.3, J9.3, J10.3, J11.3, J12.3
unnamed: J7.4, J7.5, J8.4, J8.5, J9.4, J9.5, J10.4, J10.5, J11.4, J11.5, J12.4, J12.5, J13.1, J13.2, J14.1, J14.2, J15.1, J15.2, J16.1, J16.2, J17.1, J17.2, J18.1, J18.2, J30.2
unnamed: J13.3, J14.3, J15.3, J16.3, J17.3, J18.3
unnamed: J13.4, J13.5, J14.4, J14.5, J15.4, J15.5, J16.4, J16.5, J17.4, J17.5, J18.4, J18.5, J19.1, J19.2, J20.1, J20.2, J21.1, J21.2, J22.1, J22.2, J23.1, J23.2, J24.1, J24.2, J30.3
unnamed: J19.3, J20.3, J21.3, J22.3, J23.3, J24.3
unnamed: J19.4, J19.5, J20.4, J20.5, J21.4, J21.5, J22.4, J22.5, J23.4, J23.5, J24.4, J24.5, J30.4
unnamed: J31.1, J31.2, J31.3, J31.4, J34.1, J34.2, U1.6 (I6), U1.7 (I7)

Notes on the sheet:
Lion Battery Module
July 2020
12V
16V
GND

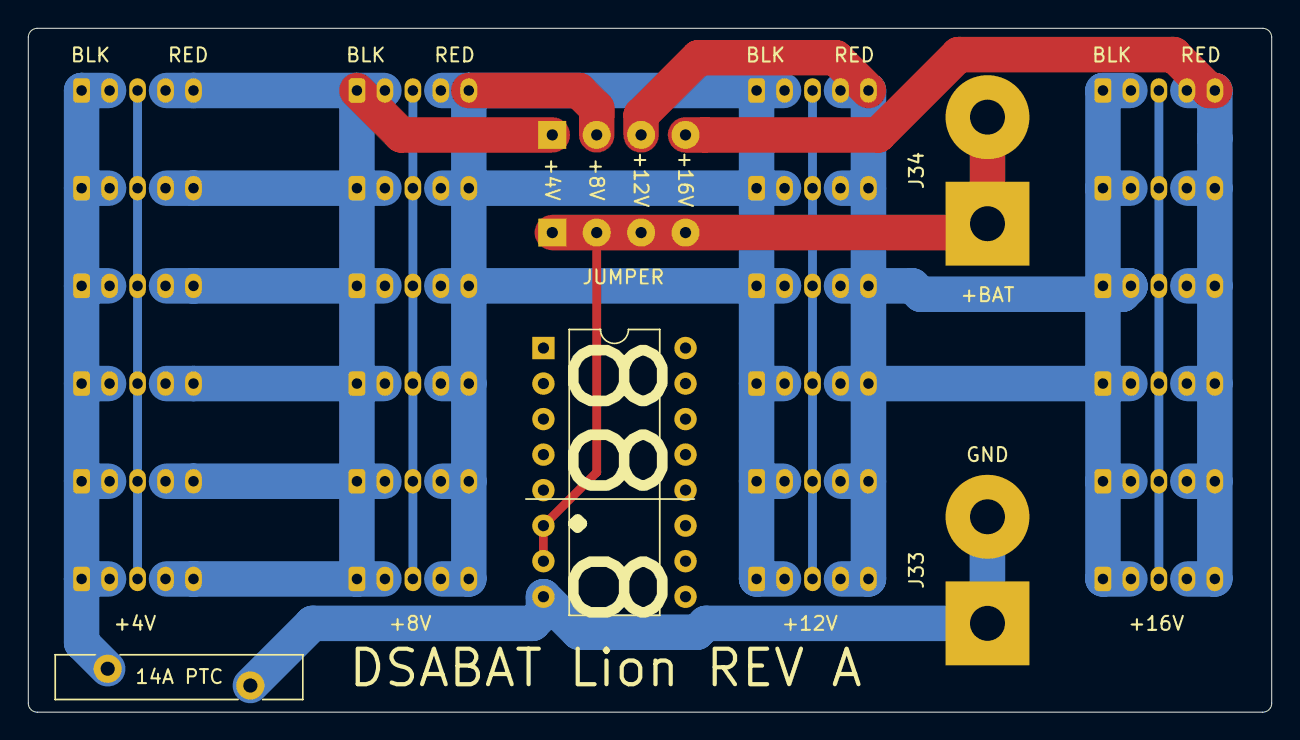
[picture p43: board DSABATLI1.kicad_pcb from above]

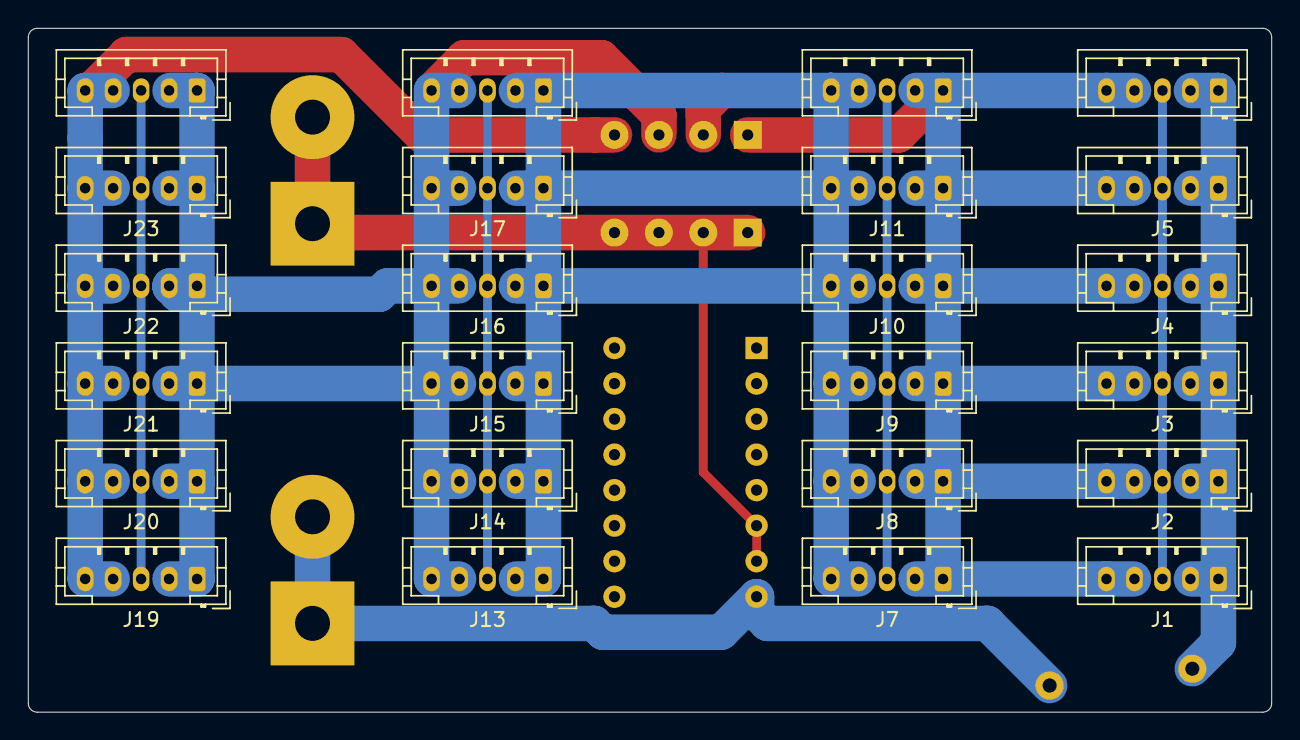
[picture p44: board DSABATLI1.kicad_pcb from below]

Board: 2 copper layers, 88.9 x 48.9 mm, 30 parts (24 on the bottom side), 11 nets.

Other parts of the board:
14A PTC: Polyfuse; Fuse_Bourns_MF-RHT1000

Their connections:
unnamed 0: 14A PTC.1; also elsewhere on the board
unnamed 1: 14A PTC.2; also elsewhere on the board

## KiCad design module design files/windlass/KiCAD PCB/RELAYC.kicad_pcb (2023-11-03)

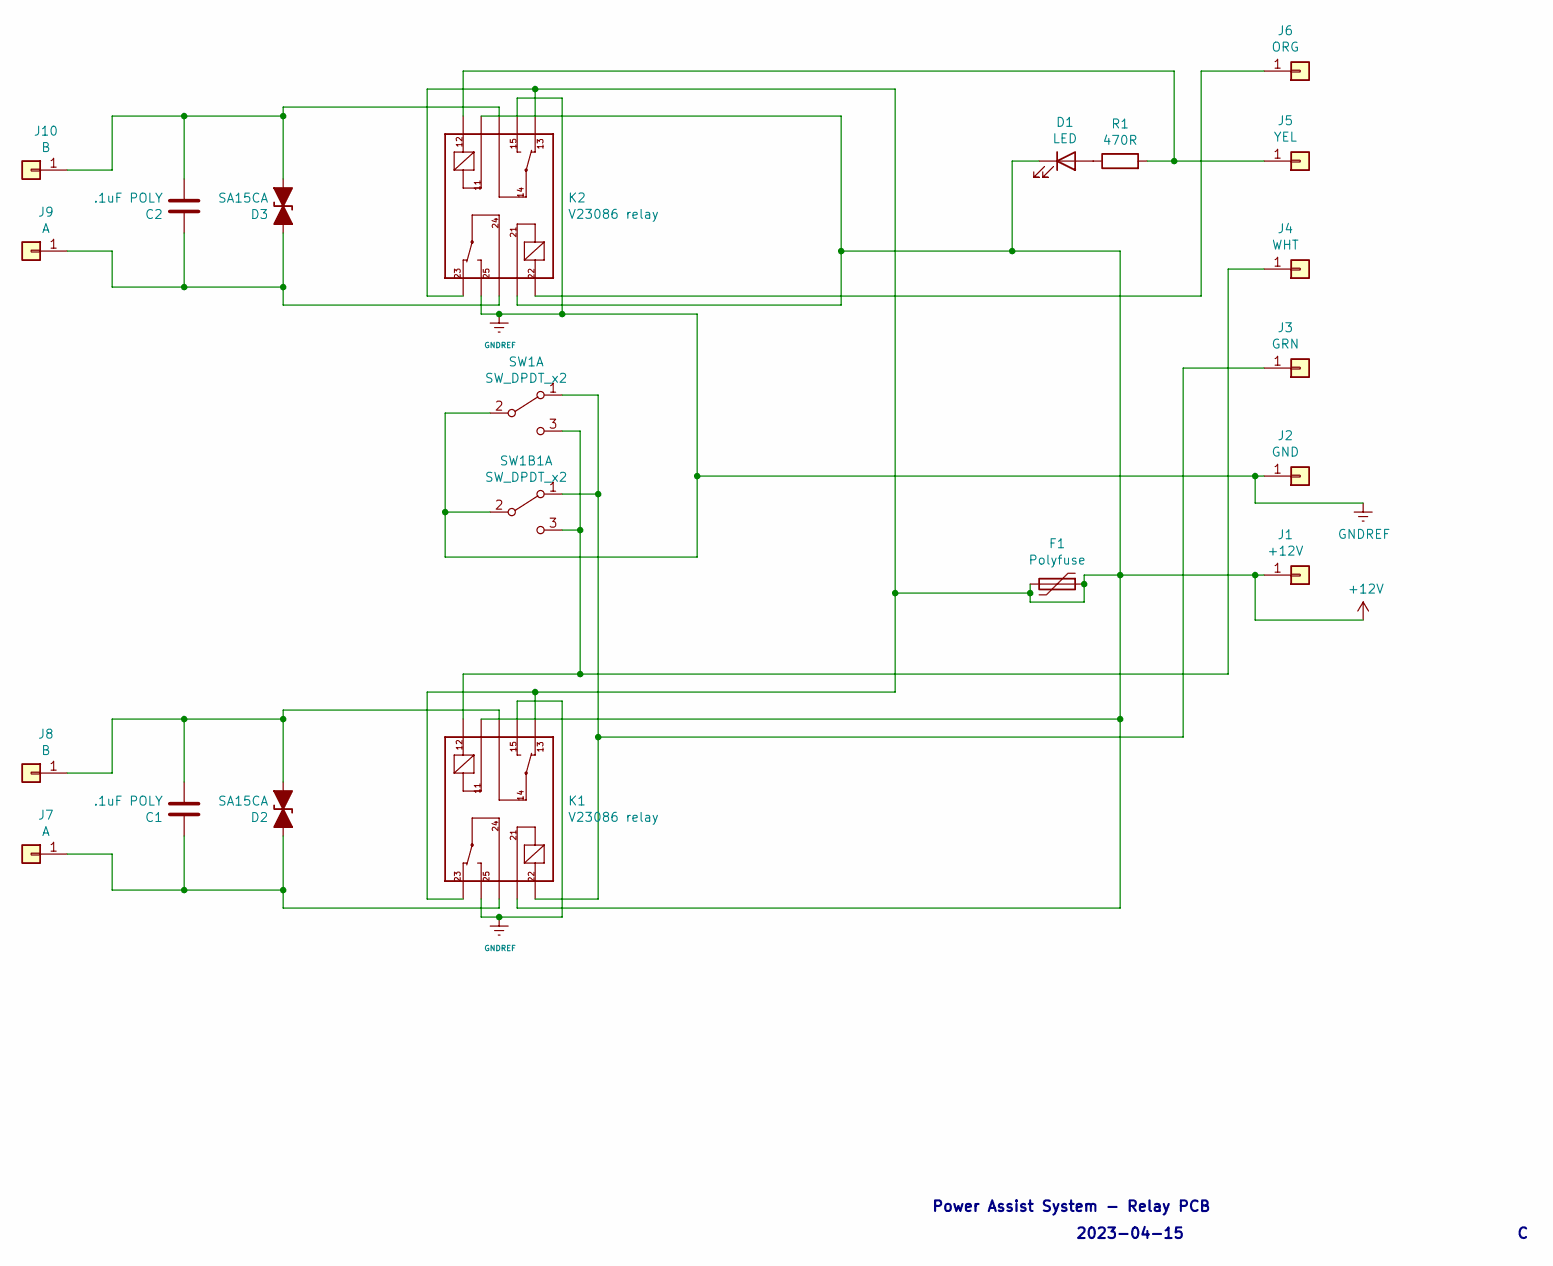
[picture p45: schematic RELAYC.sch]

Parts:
C1, C2: .1uF POLY; C_Disc_D8.0mm_W2.5mm_P5.00mm
D1: LED; LED_D5.0mm
D2, D3: SA15CA; D_T-1_P12.70mm_Horizontal
F1: Polyfuse; R_Axial_DIN0207_L6.3mm_D2.5mm_P10.16mm_Horizontal
J1: +12V; 250spadeconn
J2: GND; 250spadeconn
J3: GRN; 250spadeconn
J4: WHT; 250spadeconn
J5: YEL; 250spadeconn
J6: ORG; 250spadeconn
J7, J9: A; 250spadeconn
J8, J10: B; 250spadeconn
K1, K2: V23086 relay; RELAY_V23086C2001A403
R1: 470R; R_Axial_DIN0207_L6.3mm_D2.5mm_P10.16mm_Horizontal
SW1, SW1B1: SW_DPDT_x2; DPDT_SW

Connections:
+12V: D1.1 (K), F1.1, F1.2, J1.1, K1.11, K1.13, K1.21, K1.23, K2.11, K2.13, K2.21, K2.23
GNDREF: J2.1, K1.15, K1.25, K2.15, K2.25, SW1.2 (B), SW1B1.2 (B)
unnamed: C1.1, D2.1 (A1), J7.1, K1.24
unnamed: C1.2, D2.2 (A2), J8.1, K1.14
unnamed: C2.1, D3.1 (A1), J9.1, K2.24
unnamed: C2.2, D3.2 (A2), J10.1, K2.14
unnamed: D1.2 (A), R1.1
unnamed: J3.1, K1.22, SW1.1 (A), SW1B1.1 (A)
unnamed: J4.1, K1.12, SW1.3 (C), SW1B1.3 (C)
unnamed: J5.1, K2.12, R1.2
unnamed: J6.1, K2.22

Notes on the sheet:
2023-04-15
Power Assist System - Relay PCB

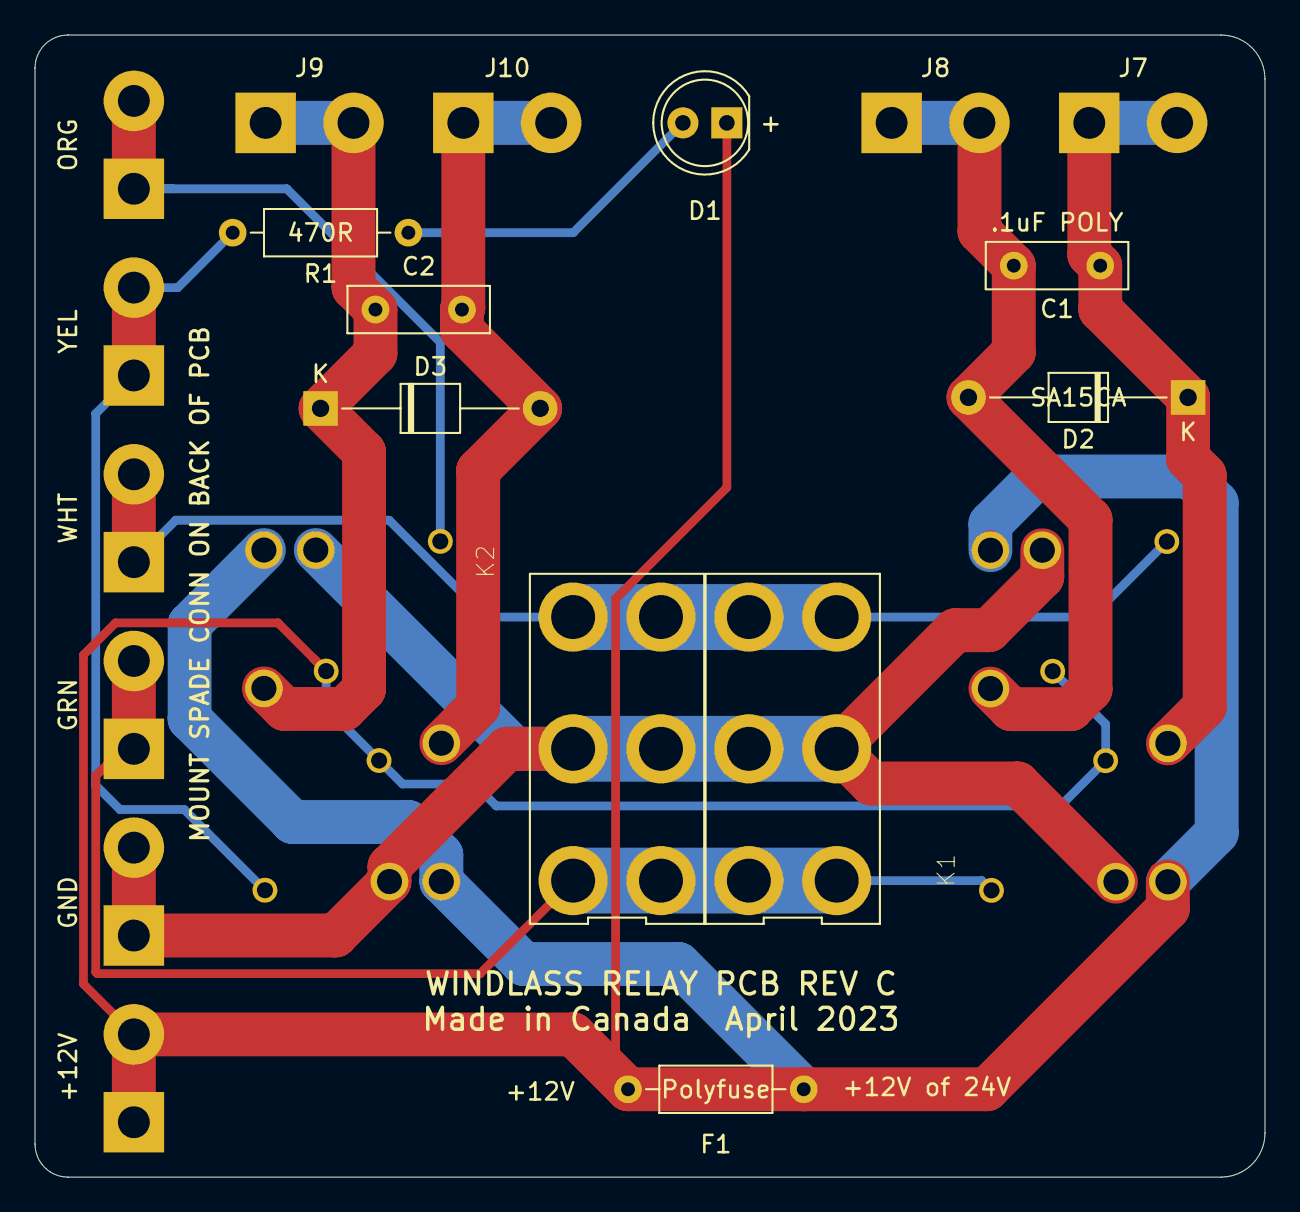
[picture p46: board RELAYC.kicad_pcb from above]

Board: 2 copper layers, 71.1 x 66.0 mm, 21 parts (0 on the bottom side), 11 nets.

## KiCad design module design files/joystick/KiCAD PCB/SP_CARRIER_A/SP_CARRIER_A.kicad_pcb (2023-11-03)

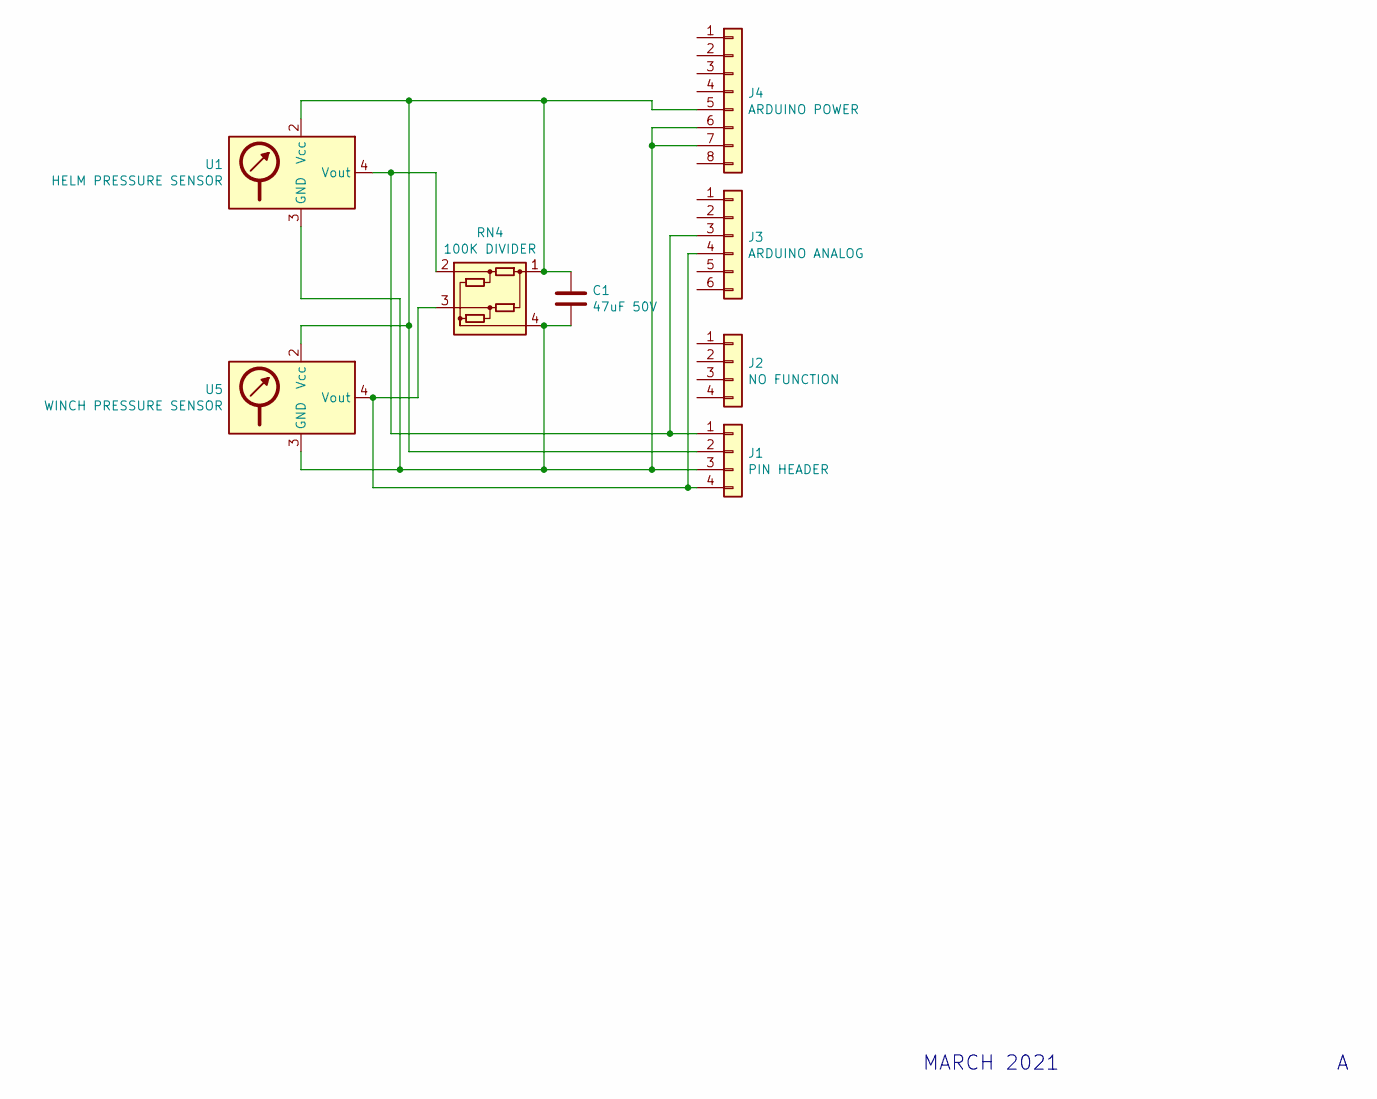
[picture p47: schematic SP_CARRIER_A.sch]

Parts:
C1: 47uF 50V; C_Disc_D8.0mm_W2.5mm_P5.00mm
J1: PIN HEADER; PinHeader_1x04_P2.54mm_Vertical
J2: NO FUNCTION; PinHeader_1x04_P2.54mm_Vertical
J3: ARDUINO ANALOG; PinHeader_1x06_P2.54mm_Vertical
J4: ARDUINO POWER; PinHeader_1x08_P2.54mm_Vertical
RN4: 100K DIVIDER; R_Array_SIP4
U1: HELM PRESSURE SENSOR; MPXV7007
U5: WINCH PRESSURE SENSOR; MPXV7007

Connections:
unnamed: C1.1, J1.2, J4.5, RN4.1 (COM1), U1.2 (Vcc), U5.2 (Vcc)
unnamed: C1.2, J1.3, J4.6, J4.7, RN4.4 (COM2), U1.3 (GND), U5.3 (GND)
unnamed: J1.1, J3.3, RN4.2 (R1), U1.4 (Vout)
unnamed: J1.4, J3.4, RN4.3 (R2), U5.4 (Vout)

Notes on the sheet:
MARCH 2021

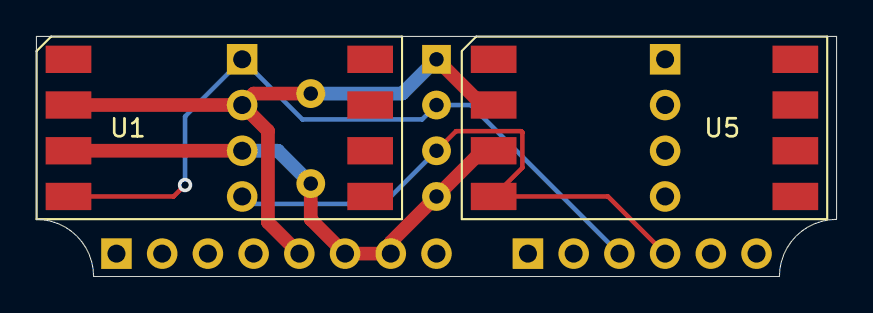
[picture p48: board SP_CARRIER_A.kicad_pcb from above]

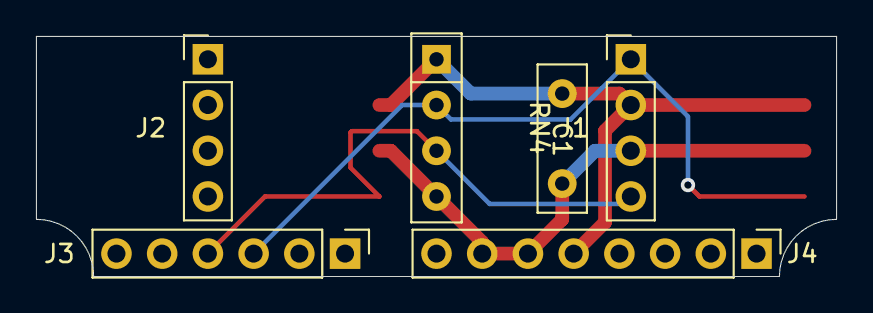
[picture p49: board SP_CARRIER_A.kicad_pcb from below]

Board: 2 copper layers, 44.5 x 13.3 mm, 8 parts (6 on the bottom side), 4 nets.

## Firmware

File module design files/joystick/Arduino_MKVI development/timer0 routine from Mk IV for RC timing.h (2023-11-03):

#include <16c74b.h>
#fuses HS,WDT,NOPROTECT,PUT,NOBROWNOUT
#use delay(clock=20000000, restart_wdt)
#include <stdlib.h>
#include <pins.h> 		// defines descriptive names for PIC pin numbers

/*******************
* LESKIW - defines *
*******************/
enum {
	BLINK_TIMER,		// mode lamp timer
	HEARTBEAT_TIMER, 	// Controls how the flashing works
	MODE_TIMER,     	// "NO ACTIVITY" TIMER, SWITCHES BACK TO WINCH MODE AFTER FIVE SECONDS
	NO_RC_PULSE_TIMER,	// IF RC PULSE NOT RECEIVED WITHIN "X" MSECS, RESETS RC PARAMETERS TO NEUTRAL
	ACK_TIMER,
	STUCK_KEY_TIMER, 	// THIS INDICATES THAT ONE OR MORE KEYS IS STUCK "DOWN" FOR MORE THAN 10 SECONDS
	BATTERY_TEST_TIMER, 	// BATTERY CONDITION IS CHECKED EVERY TEN SECONDS
	low_battery_timer,	// WHEN BATTERY REACHES CRITICAL LEVEL, THIS TIMER INTEGRATES CONDITION FOR 3 MINUTES
	NUM_TIMERS    		// this must be the last in the list
};

#define MODE_TIME 88		// initial value for mode timer (approx 5 seconds)

#define NUM_MODES  3		// FABES - max number of modes handled by this version of firmware
#define STEER_MODE 0		// rudder mode
#define WINCH_MODE 1		// winch mode
#define RIG_MODE   2		// not used in Mk IV
//#define OUTH_MODE  3		// not used in Mk IV
//#define BOOM_MODE  4		// not used in Mk IV

#define dssaDevice 0x10		// (NOT USED) make autohelm address 0x10

#BYTE	TMR0	= 0X01		// DEFINE TIMER0 REGISTER (DIRECT ACCESS)
#BYTE 	OPTION 	= 0X81 		// Port B Option register (for setting port B pullup option)
#BYTE 	INTCON 	= 0X8B 		// Interrupt control register (used to force Interrupt mask set-up)

#BYTE	PR2 	= 0X92		// DEFINE PWM CONTROL REGISTERS (DIRECT ACCESS)
#BYTE	CCPR1L 	= 0X15
#BYTE 	CCPR2L 	= 0X1B
#BYTE	TMR2 	= 0X11
#BYTE	T2CON 	= 0X12
#BYTE 	CCP1CON = 0X17
#BYTE 	CCP2CON = 0X1D

/**********************
* Function Prototypes *		// ALVEY - THESE ALLOW SUBROUTINE CODE SEGMENTS TO BE RECOGNIZED WHEREVER THEY ARE IN FILE
**********************/
void allOff(void);
void RCOff(void);
void initialize(void);
void buildModeTable(void);
char checkInputs(void);
void handleInputCommand(void);
void linkRemote(void);
void check_battery_level(void);
void beep(char numBeeps);
void batteryMeterFlashRoutine(void);
void ledsOff(void);
void restoreModeLEDs(void);
void changeMode(char newMode);
void checkJoy(void);
void checkRC(void);
void checkRF(void);
void rudstbd(void);
void rudPort(void);
void winchIn(void);
void winchOut(void);
void rigIn(void);
void rigOut(void);
void r_output_high(char sense);
void r_output_low(char sense);
void handleBeeps(void);

/*******************
* LESKIW - globals *
*******************/
char INPUT_FLAGS 	= 0;			// various control flags
#BIT STCR 		= INPUT_FLAGS.0		// 1 = sea talk command received
#BIT JOY_ENABLED 	= INPUT_FLAGS.1		// 1 = joystick is enabled
#BIT KEY_DOWN 		= INPUT_FLAGS.2		// 1 = not used in MAIN 2.0
#BIT BEEP_SENSE 	= INPUT_FLAGS.3		// 1 = identifies that sound is on
#BIT OVERCURRENT_FLAG 	= INPUT_FLAGS.4		// 1 = (not used) identifies overcurrent condition detected
#BIT PWM2_MODE 		= INPUT_FLAGS.5		// 1 = identifies PWM2 MODE (uses WINCH_IN and WINCH_OUT to control second PWM driver)
#BIT RF_MODE 		= INPUT_FLAGS.6		// 1 = identifies RF keyfob in use

signed int J_REF;				// joystick reference value, read from A/D input pin RA3
int joystick_UDvalue=0;				// calculated joystick UD PWM1 value
int joystick_RLvalue=0;				// calculated joystick RL PWM2 value

signed long RC_NEUTRAL = 117;			// RC reference value, equivalent to 1.5msec pulsewidth (calc = 117)
signed long max_pulse_length = 156;		// longest valid pulse length is 2.0 msec (approx 156 Timer0 ticks)
signed long min_pulse_length = 78;		// shortest valid pulse length is 1.0 msec (approx 78 Timer0 ticks)
signed long RC_RL;
signed long RC_UD;

char RC_FLAGS = 0;
#BIT RC_input_received 	= RC_FLAGS.0		// 1 = one (or more) RC input pulse measured to be handled in MAIN
#BIT bad_RC1_pulse 	= RC_FLAGS.1
#BIT bad_RC2_pulse 	= RC_FLAGS.2
#BIT RC_MODE 		= RC_FLAGS.3		// 1 = identifies RC MODE (uses WINCH_IN and WINCH_OUT to generate RC PWM pulses)
#BIT RF_input_received 	= RC_FLAGS.4		// 1 = one (or more) RC input pulse measured to be handled in MAIN

char JOY_POS 		= 0;			// contains joystick position flags
#BIT JUP 		= JOY_POS.0		// 
#BIT JDOWN 		= JOY_POS.1		//
#BIT JRIGHT 		= JOY_POS.2		//
#BIT JLEFT 		= JOY_POS.3		//

int debug = 0;					// holds debug flag, to control location of debug "beeps" in code
char debounce = 0;				// holds debounce flag for debug routine "button" presses

char mode = 0;					// holds current operating mode
char NUM_BEEPS = 0;				// holds number of time to beep depending on current mode
char BEEP_TIMER = 0;				// time between beeps
signed int JOY_RL_LIMIT = 20;			// joystick RL dead band
signed int JOY_UD_LIMIT = 30;			// joystick UD dead band

int timerList[NUM_TIMERS];			// define timer list
char modeList[NUM_MODES];			// define (operating) mode list

char RIG_IN = RIG_IND;				// define rig_in as pin number associated with Rig In Direction
char RIG_OUT = RIG_OUTD;			// NOTE; direction of RIG_IN can be changed at any time by pressing AUX and 
						// RIGHT FUNCTION button at the same time

char global_flags = 0;				// used to store global boolean values
#BIT watchDogAlarm = global_flags.0		// if set, the main software is stuck in a loop
#BIT rightFuncDisabled = global_flags.1		// IF SET, RIGHT FUNCTION KEY IS DISABLED
#BIT leftFuncDisabled = global_flags.2		// IF SET, LEFT FUNCTION KEY IS DISABLED
#BIT auxDisabled = global_flags.4		// IF SET, AUX KEY DISABLED
#BIT use_pwm_ramp = global_flags.5 		// IF SET, means accelerate PWM to full speed using a ramp
#BIT beepPriority = global_flags.6 		// IF SET, beep() will ignore new beeps until the current set is done
#BIT timer1_overflow = global_flags.7 		// IF SET, RC2 pulse boundary condition; ignore current pulse timing

/**************************************************
* FABES - INITIALIZE MK IV BATTERY METER FUNCTION *
**************************************************/
char battery_level = 5; 			// initialize battery to be full, EF
char read_battery = 1; 				// initialize to not read the battery level, EF
char battery_too_low = 0; 			// initialize to battery is fine, EF
char beep_flag = 0; 				// beep when battery level is low, EF


/**********************************************
* LESKIW - initialization routine (MAIN LOOP) *
**********************************************/
void initialize(void)
{
	int i;

	#USE FAST_IO(A)
	#USE FAST_IO(B)
	#USE FAST_IO(C)
	#USE FAST_IO(D)
	#USE FAST_IO(E)
	
	disable_interrupts(global);	// disable interrupts during initialization

	set_tris_a(0x1f);  		// MK IV hardware
	set_tris_b(0xc5);   		// ALLOW RC INPUTS ON PIN 33 AND 40
	set_tris_c(0x80);		
	set_tris_d(0xf3);		// 
	set_tris_e(0x06);

	allOff();			// TURN ALL OUTPUTS OFF
	LEDSoFF();			// TURN ALL LEDS OFF

	output_high(BUZZER);		// TEST BUZZER

	output_low(AUX2_RC_LED);	// LED TEST SEQUENCE
	output_low(WINDLASS_LMP);
	delay_ms(200);

	output_high(AUX2_RC_LED);
	output_low(AUX1_RELAY_LED);
	output_high(WINDLASS_LMP);
	delay_ms(200);

	output_high(AUX1_RELAY_LED);
	output_low(WINCH_LED);		
	output_low(WINDLASS_LMP);
	delay_ms(200);

	output_high(WINCH_LED);		
	output_low(HELM_LED);
	output_high(WINDLASS_LMP);
	delay_ms(200);

	output_high(HELM_LED);
	output_low(HEARTBEAT_LED);	
	output_low(WINDLASS_LMP);
	delay_ms(500);

	output_high(WINDLASS_LMP);

	output_low(BUZZER);		// end LED test

	for(i = 0; i < NUM_TIMERS; i++)
		timerList[i] = 0;

	for(i = 0; i < NUM_MODES; i++)
		modeList[i] = 0;

	setup_timer_0(RTCC_INTERNAL|RTCC_DIV_64);	// COMPILER DOES NOT SEEM TO WORK; BELOW IS DIRECT REGISTER SET-UP OF TIMER 0

//	OPTION = 0XC5;					// timer0 is loaded on RC1 pulse edge and used to time RC pulses (as a simple counter)
							// INTERNAL SOURCE, PRESCALE = 64; NO PORTB PULL-UPS
	disable_interrupts(int_timer0);			// we do NOT want timer0 interrupts to be generated

	setup_timer_1(T1_INTERNAL|T1_DIV_BY_4); 	/* timer1 is primary real time clock; interrupts every 52 msec */
	enable_interrupts(INT_TIMER1);			// timer1 is also used in relative mode to time RC pulsewidths

	ext_int_edge(L_to_H);				// SET RB0 INTERUPT TO TRIGGER ON RC1 RECEIVER INPUT 
	enable_interrupts(INT_EXT); 			// interupt EXT is used to synchronize with rising edge of RC1 pulse
	enable_interrupts(INT_RB); 			// interupt RB is used to synchronize with rising edge of RC2 pulse
							// **** interupts are enabled alternately, so that each pulse gets exclusive use of Timer0

	PR2 = 0XFF;				// SET TMR2 COMPARE VALUE TO "255" STEPS (max PWM resolution)
	CCPR1L = 0;				// INITIALIZE PWM1 PULSE WIDTH TO 0
	CCPR2L = 0;				// INITIALIZE PWM2 PULSE WIDTH TO 0
	TMR2 = 0X10;				// INITIALIZE PWM FREQUENCY AT 20 KHZ (20 MHZ / 4/ 256)
	T2CON = T2CON | 0X04;			// TURN ON PWM2 CONTROL REGISTER, WITH NO PRE/POST SCALE VALUES

	setup_adc(ADC_CLOCK_DIV_8);
	setup_adc_ports(RA0_RA1_RA3_ANALOG);	// SET UP A/D PORTS FOR JOYSTICK AND BATTERY METER
	set_adc_channel(3);
	delay_ms(100);
	J_REF = read_adc();			// SET JOYSTICK REFERENCE VALUE (ONCE, AT POWER-UP)

	if (INPUT(PUMP_SW))			// JOYSTICK DISABLED IF LOWER LEFT SWITCH PRESSED (0) ON POWER-UP
		JOY_ENABLED = 1;
		BEEP (3);

	enable_interrupts(global);		// enable all defined interrupts

//	INTCON = 0XD8;				// enable external and Port B interrupts (forced)
}








/****************************************
* RRRRR    CCCC   1  I N     N  TTTTTTT * THIS INTERUPT SYNCHRONIZES WITH RISING EDGE OF THE
* R    R  C    C  1  I N     N     T    * RC1 PULSE, AND MEASURES WIDTH FROM 1.0 - 2.0 MSECS
* R    R  C       1  I N N   N     T    *	
* RRRRR   C       1  I N  N  N     T    * TIMER1 IS USED IN RELATIVE MODE TO TIME PULSES 
* R  R    C       1  I N   N N     T    *   
* R   R   C    C  1  I N    NN     T    * TWO TIMER1 READINGS ARE TRANSLATED TO A PWM VALUE AND A DIRECTION
* R    R   CCCC   1  I N     N     T    * NOTE THAT INT_EXT AND INT_RB ARE ENABLED ALTERNATELY, SO THAT EACH ROUTINE GETS TO USE TIMER0
****************************************/

#int_ext
void timeRC1pulse(void)
{
	signed long RC1_stop = 0;				// MUST INITIALIZE RC1_STOP TO 0

//	disable_interrupts(int_ext);
//	disable_interrupts(int_rb);

	set_timer0(0);						// reset Timer0 to start pulse timing count
	timerList[NO_RC_PULSE_TIMER] = 2;			// reset NO_RC_PULSE_TIMER to 100 msec
	delay_us(100);						// debounce RC1 pulse START

	while (input(RC1_INPUT))				// debounce, and stay here for 1 - 2 msec to time RC1 pulse
	{
		restart_wdt();
		RC1_stop = get_timer0();			// AMPLIFY RESULT BY ADDING "8" COUNTS
		if (RC1_stop > max_pulse_length)
		{
			bad_RC1_pulse = 1;			// validate pulse length to be < 2.0 msec
			beep(1);				// BEEP if bad pulse detected
			break; 
		}
	}
	if (RC1_stop < min_pulse_length) 
	{
		bad_RC1_pulse = 1;				// validate pulse length to be > 1.0 msec
		beep(1);					// BEEP if bad pulse detected
	}
	else
	{
		RC_RL = ((signed long) RC_NEUTRAL - RC1_stop);	// calculate RC1 offset time and return
		RC_RL <<=1;					// amplify RC_RL by factor of 2 (same scale as joystick)
	}
//	enable_interrupts(int_rb);
}



/*********************************************
* RRRRR    CCCC    2222   I N     N  TTTTTTT * THIS INTERUPT SYNCHRONIZES WITH RISING EDGE OF 
* R    R  C    C  2    2  I N     N     T    * THE RC2 PULSE, AND MEASURES WIDTH FROM 1.0 - 2.0 MSECS
* R    R  C           2   I N N   N     T    *	
* RRRRR   C          2    I N  N  N     T    * TIMER1 IS USED IN RELATIVE MODE TO TIME PULSES 
* R  R    C         2     I N   N N     T    *   
* R   R   C    C   2      I N    NN     T    * TWO TIMER1 READINGS ARE TRANSLATED TO A PWM VALUE AND A DIRECTION
* R    R   CCCC   222222  I N     N     T    * NOTE THAT INT_EXT AND INT_RB ARE ENABLED ALTERNATELY, SO THAT EACH ROUTINE GETS TO USE TIMER0	
*********************************************/

#int_rb								// 01/07/05 this interrupt WORKS...
void timeRC2pulse(void)
{
	signed long RC2_stop = 0;				// MUST INITIALIZE RC2_STOP TO 0
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

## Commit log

2023-11-03 initial upload
    [027-2014-04 - Windlass Hub.SLDDRW, 027-2014-04 - Windlass Hub.SLDPRT, 375RADIALPORT - Radial Ported Body.SLDPRT, 375RADIALPORT - Radial Ported Body.SLDPRT.SLDD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]
2023-11-04 File structure clean-up
    General reorganization and clean-up of file structure and file names. No file content changed
    [DSABATLI1-B_Cu.gbr, DSABATLI1-B_Mask.gbr, DSABATLI1-B_Paste.gbr, DSABATLI1-Edge_Cuts.gbr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]
2023-11-25 clean up with Meister S
    [027-2014-04 - Windlass Hub.SLDDRW, 027-2014-04 - Windlass Hub.SLDPRT, 375RADIALPORT - Radial Ported Body.SLDPRT, 375RADIALPORT - Radial Ported Body.SLDPRT.SLDD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]
